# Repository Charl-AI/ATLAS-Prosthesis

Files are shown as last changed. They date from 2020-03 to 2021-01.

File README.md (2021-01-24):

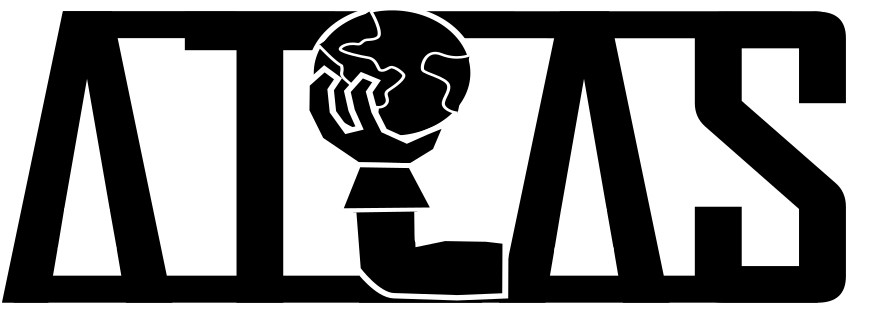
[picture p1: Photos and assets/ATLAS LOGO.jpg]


Modern solutions for control of prosthetic hands involve sensing intentional muscle contractions using myoelectric (EMG) muscle sensing. Unfortunately this is expensive - with modern electro-mechanical prostheses starting at around £ 10 000 - and sensitive to issues such as perspiration and sensor placement.

ATLAS is a novel prosthetic hand using mechanomyographic (MMG) muscle sensing to control the device. It is fully 3D printable and can be manufactured for under £ 300. The only requirements for reproducing this project are access to a 3D printer (such as the Creality Ender 3 that we used, £ 150) and a soldering station (roughly £ 10).

This project was completed as a university project by four members (and achieved an A grade) and there is plenty of scope for people to adapt and improve our work. The project is documented on this page, however, names and identifying information about the group members have been redacted in some places for privacy.



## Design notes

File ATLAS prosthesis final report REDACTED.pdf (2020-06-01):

## Design, Make & Test Project:

# Final Report

### Mechanomyographic-controlled prosthetic hand

78 Pages | 03/06/20

Group 19

Supervisor:

Charles Jones

Page ii

EXECUTIVE SUMMARY

Transradial (below elbow) amputation can be a debilitating condition, making many tasks associated

with daily life considerably more difficult for amputees. Prosthetic hands aim to mitigate this issue

by providing amputees with a device which can assist in performing complex functions such as

grasping objects. However, the limiting factor in upper body prosthetic design has long been the

shortfall in control systems, preventing amputees from controlling complex machines such as fully

articulated prosthetic hands. Modern solutions to this problem primarily involve using

electromyographic (EMG) sensing to pick up on intentional muscle signals and control the device,

although this method has considerable disadvantages such as perspiration and sensor placement

affecting the results. Moreover, EMG solutions on the market today start at a prohibitively expensive

price point of around £ 10,000. This design, make and test project introduces ATLAS, a novel solution

using mechanomyographic (MMG) muscle sensing to control the device (shown in Figure 1). The

prosthetic hand can form three user-controlled grip poses (point, grasp, and open), controlled

through a specially designed MMG-sensing armband which was demonstrated to produce up to

90 % muscle sensing accuracy when tested virtually with a dataset of 17 labelled muscle movements

over 6 different muscles. The mechanical design of ATLAS draws from fields such as soft robotics and

biomimetic design, using a composite structure that enables grasping of a variety of hard, soft and

irregularly shaped items with robust functionality: in testing, ATLAS was able to pick up objects of

over 3.5 kg with ease. ATLAS is fully 3-D printable and can be manufactured for under £240, lending

itself to an open-source, distributed manufacture model of production, specifically intended to be of

most benefit to amputees in developing countries and children. Unfortunately, the unprecedented

coronavirus outbreak cut short the practical time available for this project, however, all possible

steps were taken to mitigate this effect and an alternative work package was completed to ensure

the project remained of high quality despite these setbacks.

Figure 1: ATLAS (without electronics or sensors)

Page iii

CONTENTS

Executive Summary | ii
Contents | iii
Acknowledgements | iv
1 | Introduction | 1
1.1 | Brief | 1
1.2 | Team Roles | 1
1.3 | Report Structure | 2
2 | Literature Review and project background | 3
2.1 | Transradial amputations and needs of amputees | 3
2.2 | Principles and paradigms of upper body prostheses | 3
2.3 | Mechanomyographic techniques for muscle sensing | 5
3 | Design | 7
3.1 | Product Design Specification | 7
3.2 | Expert Research Meetings | 9
3.3 | Conceptual Design | 10
3.4 | Mechanical Design | 14
3.5 | Control Design | 23
3.6 | Electronic Design | 31
3.7 | Final Design | 36
4 | Manufacture and Assembly | 37
4.1 | Methods and Justification | 37
4.2 | Mechanical characteristics of FDM printed parts | 38
4.3 | Design for 3-D Printing | 38
4.4 | Printing with PETG, PLA and TPU | 42
4.5 | Assembly of electronics | 43
4.6 | Overall assembly | 43
5 | Product Cost and Budget | 45
5.1 | Finance and budgets | 45
5.2 | Final Product Cost | 45
6 | Testing and Design Verification | 47
6.1 | Destructive Testing | 47
6.2 | Grip Strength Test | 50
6.3 | User Testing | 51
7 | Alternative Work Package | 52
7.1 | Effect of early university shutdown on project | 52
7.2 | Details of uncompleted tasks | 52

Page iv

7.3 | Details of alternative work package | 53
7.4 | Alternative Work | 53
8 | Discussion | 59
8.1 | PDS Evaluation | 59
8.2 | General Discussion | 61
8.3 | Future Work | 64
9 | Conclusions | 65
10 | Personal Reflective Reviews | 66
10.1 | | Error! Bookmark not defined.
10.2 | | 67
10.3 | | Error! Bookmark not defined.
10.4 | | Error! Bookmark not defined.
11 | References | 70

ACKNOWLEDGEMENTS

The group would like to extend our warm thanks to the following people and companies:

1 | INTRODUCTION
1.1 | BRIEF

Today’s market for upper body prosthetics is broadly divided into high-cost, high

sophistication, electro-mechanical designs, and low-cost body-powered devices with less

functionality (elaborated upon in the literature review, section 2). This project aims to bring the

advantages of electromechanical prostheses to consumers at a significantly lower price point by

exploiting two emerging techniques: mechanomyographic (MMG) muscle sensing and open source

distributed manufacturing. At the beginning of the project, the following five targets were set out:

- Design and manufacture a prosthetic hand capable of forming multiple useful grip patterns.
- Design a comfortable strap to house muscle sensors and a basic socket to suspend the

device from a demonstration stand.

- Sense and analyse MMG muscle signals, producing an algorithm to accurately classify muscle

contractions.

- Implement a control system so the user can accurately move between the grip patterns by

utilising intentional muscle movements.

- The final product must be manufacturable by volunteer engineers or hobbyists at a low

price.

These ambitious targets are designed to enable the creation of a new class of prosthetic device –

one which can bring the functionality associated with high-cost prostheses but be open-sourced

and manufactured at a low cost by amputees themselves or volunteers.

1.2 TEAM ROLES

Although all members of the team contributed to many aspects of the project, and supported each

other wherever necessary, a summary of primary roles are listed below, together with the headline

requirements and responsibilities of the role. Team members had a management role which

supported the organisation of the team and project, as well as a technical role. These were allocated

based on previous project experience, areas team members wanted to focus on, and ME1/2/3

module experience, and are listed below in Table 1.

Table 1: Team roles and responsibilities

Name | Management Role | Technical Role
| Project Manager | Electrical Lead
| Ultimately responsible for ensuring all elements of | Lead for the design, testing, build and
| the project progress on track and to a suitable | assembly of physical electronics.
standard, in line with internal and external
deadlines, and allocating resources to ensure that
deadlines are met.
Meeting Coordinator
In charge of organising group meetings and room bookings.

Manufacturing Lead
Responsible | for | manufacture | and
printing, and also for providing input on design for additive manufacturing to the mechanical design process.
| Procurement + Finance Lead | Mechanical Design Lead
| Responsible for managing, facilitating and | Lead on design process, bringing together
| approving purchase requests (together with the | work from other team members
| PM), and ensuring expenditure remains within | regarding product design from inception
| budget and restrained. | right through to final prototype stage.
Charles
Jones

Document Lead
In control of overall document management, including Quality Plan, Progress Report and Final Report, and creating timelines to ensure these are produced on time.

Coding Lead
Responsible for all software elements of the design, from signal acquisition and processing to digital user experience design.

1.3 REPORT STRUCTURE

This report aims to present the final product, ATLAS, and the care and attention invested into all

three areas of design, make and test. It begins with a literature review, outlining the market need for

a product of this type, the background of the market, and consideration of different prosthetic

control methods. Section 3 addresses the design progression, covering the full process from

conception to detailed design of the mechanical, electrical and control systems of the device. It is

important to note that ATLAS was explicitly designed using a continuous, iterative cycle of

prototyping and testing, so this section includes many of the tests which were performed to inform

design decisions. Section 4 details the manufacture of the product, explaining the methods and

materials chosen, alongside considerations made when designing with these in mind. Section 6 then

documents the testing performed to verify design decisions, refine areas of the product and to

evaluate if the product performs as specified. This project was unusual in that it was interrupted by a

complete shutdown of practical university work in response to the unfolding pandemic COVID-19, so

a section was included to discuss the effects of the shutdown on the project and provide alternative

work to replace the work that was cut short. The discussion and conclusions follow, and the report

finishes with personal testimonials from each of the four group members

2 LITERATURE REVIEW AND PROJECT BACKGROUND

A literature review was conducted to understand modern prosthetic devices and the market for

them today – first, the prevalence of transradial (below elbow) amputations and the needs of

amputees were established and the principles and challenges of modern prosthetic design were

examined. Finally, the review covers the emergence of mechanomyography (MMG), a novel muscle

sensing technology which is used to control the ATLAS prosthetic hand made by this group.

2.1 TRANSRADIAL AMPUTATIONS AND NEEDS OF AMPUTEES

The dexterity of the human hand to perform complex mechanical tasks possesses no parallel in the

human body; it is often modelled as a machine with 27 independent degrees of freedom (1) and it

has huge versatility – giving it uses in all areas of modern life, including sports, personal care,

cooking, communication and more. The loss of a hand from a transradial amputation is an extremely

debilitating condition which typically occurs after a traumatic injury (2), and maximising quality of

life after such an injury is best achieved through a program of rehabilitation utilising prosthetic

devices to allow the patient to re-learn daily tasks (3). The needs of prosthetic device users are well

known, with studies over the previous 20 years (4,5) corroborating the same few key desires: the

ability to perform tasks such as dressing and eating with knife and fork; anthropomorphic aesthetics;

reliable, high strength grasping with their prosthesis; and comfort using the device.

2.2 PRINCIPLES AND PARADIGMS OF UPPER BODY PROSTHESES

Mechanical design of fully articulated, anthropomorphic hands is, in principle, straightforward.

These devices exist in robotics development (reviewed in (6)). However, prosthetic devices have yet

to match the ability for independent finger articulation of these robots. This is in large part due to

control systems and the interface between the user and the machine lacking the necessary

complexity to allow control in all 27 degrees of freedom. The two main control methods used in

prosthetic devices on the market today are body-powered control and electromyographic (EMG)

control.

Body-powered prostheses rely on the user providing the power and control of movement by

physically actuating the device’s mechanism (often using a harness and tension cable system which

the user pushes against). The most common type of body-powered prosthetic device is the split

hook, depicted in Figure 2(A) – these provide a durable solution which give the amputee the ability

to perform simple grasping movements. Unfortunately, however, their functionality does not extend

much further than that, which is a key reason why many amputees abandon their prostheses entirely. As many as 56 % of upper limb amputees wear their prosthetic limb ‘once in a while’ or

‘never’ and 64 % of amputees rate the functionality of them as ‘fair’ or ‘not acceptable’ (7) – this

high rejection rate, combined with the poor aesthetics of split hooks, has meant they have begun to

fall out of favour in recent years.

Electromyographic-controlled prostheses (also known as myoelectric or EMG), depicted in Figure

2(B), are a more modern solution and typically show lower rates of user rejection than body-

powered prostheses (8). These devices allow the user to control an electronically powered

prosthetic hand by using voluntary muscle contractions that are picked up by electrodes, which can

be placed on the surface of the skin, as reviewed in (9), or implanted into the user’s forearm muscles

(as in (10)). These devices typically have several pre-programmed grip patterns which the user can

move between, giving them superior functionality to body-powered prostheses. Arguably the most

significant issue with the myoelectric prostheses available on the market today is their prohibitively

high price point, typically of the order of £10,000 and upwards – naturally, this has spurred

significant research interest in developing low-cost alternatives to these products (11-13), however,

none of these lower-cost products have yet proven to be viable as a long-term solution for

amputees.

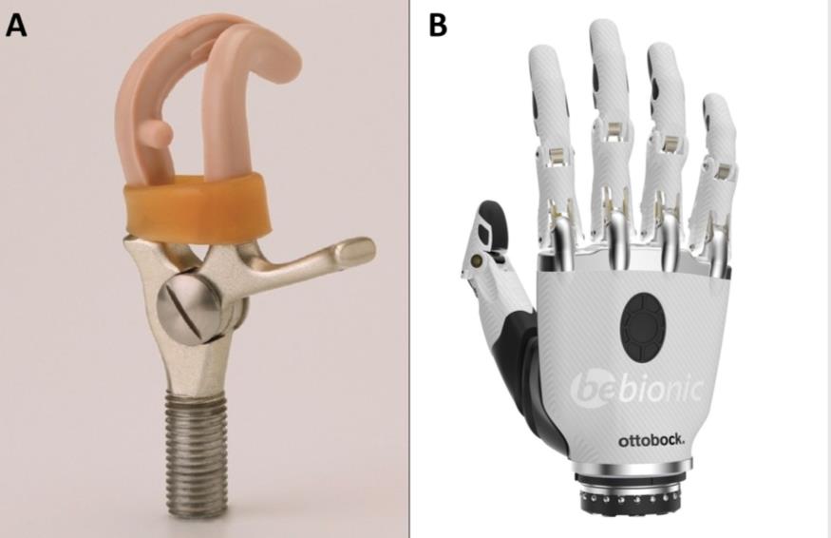
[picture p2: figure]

Figure 2: Body-powered split hook prosthesis (A), adapted from figure 2 of (14). Ottobock BeBionic myoelectric prosthesis

(B), figure from ottobockus.com (15).

Thus, amputees are today faced with a difficult choice when selecting between devices – either

choose a mechanical device with high reliability but limited functionality or have to part with

potentially tens of thousands of pounds for a myoelectric device. This problem is exacerbated when

considering that many countries do not have health services that will purchase these devices for amputees; moreover, children are often denied expensive devices because the investment is too

great for a product which they will grow out of in a couple of years. A brief comparison of several

notable myoelectric products, and a well-known open-source mechanical design, are presented

below in Table 2, illustrating the wide range of price-points and functionality.

Table 2: Comparison of variety of products on the market

Product,

[Manufacturer]

Cost | Product information

Michelangelo

hand [Ottobock]

£ 46,000 | Aesthetically pleasing design with a silicone glove for added
| realism. Hand can perform 7 pre-set grips and models the
| action of bones and joints.

Bebionic

[Ottobock]

£9,000 | The hand is capable of 14 grip patterns, with actuation on each
| individual digit, and an adjustable hand position.

Hero Arm [Open

Bionics]

£5,000 | This is the cheapest myoelectric device on the market, in part
| due to its 3-D printed design. However, it has not yet been
| approved by the NHS in the UK.

Phoenix Hand [E-

NABLE]

£50 | A 3-D printed, open source, body-powered design. Low
| functionality and low durability.

One further challenge of prosthesis design is the suspension of the device from the amputee.

Modern devices typically use one of three techniques for prosthesis suspension: self-suspended,

suction methods, and harness methods. The advantages and disadvantages of each method are

discussed in (16) and (17) provides a review on the topic of prosthetic interface and its effect on

comfort. This area of prosthetic design, however, is not the focus of this DMT project, so will not be

discussed any further in this review.

2.3 MECHANOMYOGRAPHIC TECHNIQUES FOR MUSCLE SENSING

One alternative to the paradigms of body-powered and EMG prostheses that has gained traction in

recent years is mechanomyographic-controlled (MMG) prosthetics. MMG muscle sensing relies on

sensing low-frequency, mechanical vibrations generated by muscles during a voluntary contraction

and has been shown to produce comparable results to traditional EMG sensing (18-20). Although

EMG is typically considered the gold standard for muscle sensing, MMG methods have several practical advantages that suit use in a prosthetic hand, including low sensitivity to changes in skin

impedance and low sensitivity to non-optimal sensor placement – both of which are well-known

problems with EMG sensing (21,22). The nature of MMG signals as vibrations also means that the

hardware requirements for MMG sensing are simple and low-cost, requiring only microphones with

no amplification necessary.

Despite these advantages, there have been relatively few attempts to develop a prosthetic hand

controlled by these signals, with notable research coming from Imperial College London’s

Biomechatronics laboratory (23,24). A spin-off company from Imperial, SERG technologies, has

recently begun development into this very field, so it is the authors’ hope that commercial MMG-

controlled prosthetics will become available in the coming years.

3 DESIGN

The first major step in the engineering process was the actual design of the product. Initially,

quantifiable targets for the project were set out in the PDS. From there, concepts were developed,

and a morphological analysis conducted upon the different aspects of the concepts. The design was

then split into mechanical, electrical and control streams; each being designed largely in parallel with

all sections coming together in the final design.

3.1 PRODUCT DESIGN SPECIFICATION

The first stage of the design process involved constructing a product design specification (PDS),

shown in Table 3. This was produced from the targets set out in the brief (section 1.1), using insight

gained from the literature review (section 2); the PDS sets out quantitative objectives that the

product can be designed for and tested against to ensure high quality through the design, make and

test process. Naturally, due to the number of unknowns at the beginning of the project, the PDS was

refined several times due to increased knowledge about the technical aspects of the project, a topic

elaborated upon in the project progress report and quality plan documents (25,26). Aspects which

were subject to change are marked with an asterisk and the history and reasons for the change are

more fully explained in the progress report.

Some aspects of the PDS are crucial for successful delivery of the project targets, whereas other

aspects are less important either because they do not affect the project as much or because the

objective was chosen as an arbitrary target. To create a clear demarcation between these three

levels of importance, the aspect section of the PDS was color coded, with green aspects being crucial

to the project performance, yellow aspects being important, but arbitrarily chosen goals and blue

aspects being non-critical to the delivery of the final product.

Table 3: Product Design Specification

Aspect | Objective | Justification | Verification
Number of grip poses* | ≥ 3 | Three poses should provide sufficient functionality for key uses in daily life. | Design review.
Maximum grip force | ≥ 30 N | 30 N is suitable for basic daily tasks such as carrying shopping and shaking hands. | Prototype testing using force meter.
Sensing method | MMG | MMG sensing will be used for signal acquisition. | Design review.
Gesture recognition accuracy | 90 % | For the device to be useable daily, it must correctly actuate 90 % of the time to avoid user frustration. | Prototype testing.
Battery life | 12 hours | 12 hours of continuous use would last through a full workday and use at home. | Prototype testing.
Product lifespan | 2 years | Operate for a minimum of 2 years before failure under standard use. | Fatigue testing of prototype.
Waterproofing | IP33 rating | This should allow for protection from splashes and small solid objects. | Test prototype against standards.
Form factor | Adult sized right hand | The device should fit adult transradial amputees. A basic socket will also be designed for demonstration purposes, although this is not the focus of this project. | Design review.
Mass | < 500g | An average human hand has a mass of approximately 500g. This should therefore be a reasonable upper limit for the product mass, to avoid user discomfort. | Weigh prototype with digital balance.
Maximum electronics temperature | < 40 °C | Skin-contact and external surface temperatures must remain under 40 °C to avoid potential discomfort and burns (based on ASTM C1055 standards (27)). | Run for 10 mins then scan with infrared thermometer.
Transmission enclosure | Enclosed | Transmission parts should be enclosed for the user’s safety. | Design review.
Electronics enclosure | Enclosed | Electronics should be enclosed to minimise the chances of burns and shocks. | Design review.
Loading | ≥ 50 N | The mechanism must not break when overloaded. | Perform loading test on prototype.
Quantity | ≥ 2 | An initial working prototype will be made followed by a final product. | Count prototypes.
Cost* | < £400 | If the final device has a materials cost of less than £400, it will be accessible to users with a wide range of economic circumstances. | Summing cost from bill of materials.
Materials* | Cheap and widely available materials | Material selection will occur at a later project stage and will be intertwined with the manufacturing processes chosen. | Design review.
Processes | 3-D printing and related methods | The product must be manufacturable by volunteer hobbyists and engineers using methods reasonably accessible to them. | Design review.
Assembly | < 3 hours | Must be assembled and fitted to an amputee in less than three hours by an engineer. | Timed test with stopwatch.
Training | <30 mins | New users should be able to learn the basics of controlling the system quickly to avoid frustration. | Timed test with stopwatch.

Performance

Life

Size

Safety

Production

3.2 EXPERT RESEARCH MEETINGS

Early in the design process, we decided to organise meetings with experts in fields relevant to this

project. Fortunately, both Alex Lewis and Liang He kindly offered us their time and meetings with

them yielded some extremely valuable insights into different areas of the design. The first meeting

was with Alex Lewis, a quadruple amputee who sits on the board of directors of SERG technologies

(a spin off company from Imperial focussing on the uses of mechanomyography). Liang He, who we

met in the second meeting, is a soft robotics PhD student from Imperial’s Dyson school of Design

Engineering.

3.2.1 MEETING WITH ALEX LEWIS

The key insights from the meeting with Alex were:

| • He had found that the robustness and versatility of non-mechanical prosthetics is a major
| issue; for day-to-day use, he uses a mechanical split-hook.
| • Having a prosthetic capable of multiple, simple day-to-day tasks would be beneficial.
| Examples he gave included: picking up a glass, moving a variety of objects around, or holding
| cutlery.
| • In his opinion, the performance of a prosthetic is far more important than how it looked; he
| believed that this opinion was held by most amputees, including children as well as adults.

3.2.2 MEETING WITH LIANG HE

The aim of the meeting with Liang He was to gain more of an insight into how soft robotics like those

used in medical procedures could influence a prosthetic design. The key insight was that for an

electromechanically controlled prosthetic, the stiffness of the composite finger design is a major

design variable and would need careful consideration. He also discussed haptic feedback, and the

various methods that could be delivered (through mechanical vibration, sound, or electrical

stimulation), but noted this could be a complex addition to the project. It was also noted that

electrical or mechanical stimulation near the MMG sensors could cause significant interference.

3.3 CONCEPTUAL DESIGN

During conceptual design, it is important to generate a wide range of ideas, taking many forms and

using different mechanisms and technologies to solve the same problems. This section details the

process followed when considering different concepts and ideas, using a morphological chart to aid

decision making and produce a final concept.

3.3.1 IDEATION

Figure 3 displays some early stage annotated ideas, which were then developed into the first

concepts. Some key considerations are how many digits the hand has, how the digits are actuated

and the grasping mechanism.

Figure 3: Selection of initial ideas

3.3.2 INITIAL CONCEPTS

This section introduces 3 of the most interesting concepts produced in this process. These were

influential in constructing the morphological chart, which includes aspects from each of these

concepts and more.

The first concept, shown in Figure 4, is a design with 5 digits. The 4 fingers are connected to a linear

motor with tendons and the force is distributed equally across them using a ‘whippletree’

mechanism. The thumb is actuated by a separate linear motor on the underside of the hand and the

fingers have a design of 3 phalanges per digit (meaning 3 independently articulated sections). The

benefit of this design is that by having only two motors, the cost for electronics would be low;

however, the drawback would be that there is less scope for different poses, as the four fingers

cannot be actuated independently.

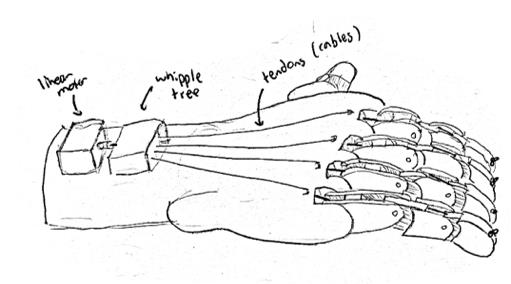
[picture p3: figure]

Figure 4: Concept 1

Figure 5 shows a second 5-digit concept. Each finger has two phalanges, which are actuated by a DC

motor using worm gears and linkages. The design also contains a rotating wrist, and a pivoting

thumb. The main benefit of this design would be the scope for many different grip poses, and the

dexterity that would provide. However, the drawback would be that the design is quite complex

mechanically and electronically, and thus likely quite expensive and difficult to manufacture.

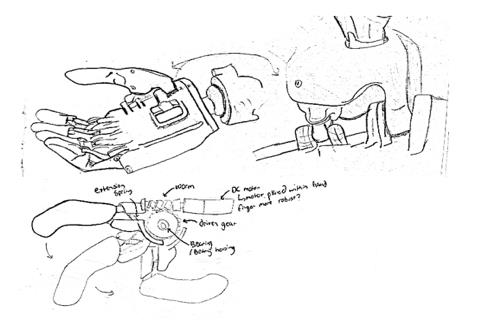
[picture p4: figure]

Figure 5: Concept 2

The third concept (Figure 6) is focussed on the digits themselves. In this concept, the fingers are

based off human biology, where hard bones lend rigidity and a soft outer skin gives grip and

durability. The advantages of this approach are self-evident as the concept could, in theory, come the closest to matching the capabilities of human fingers. There is, however, increased design

complexity and care would be necessary to tune the ratios of hard and soft material.

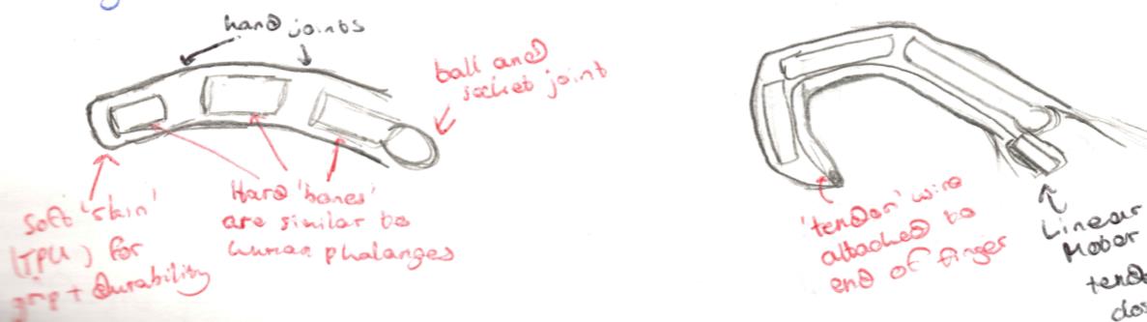
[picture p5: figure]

Figure 6: Concept 3

3.3.3 MORPHOLOGICAL ANALYSIS

After the initial conceptual design, a morphological analysis was conducted to identify the many

possible variations of the key features of the product. This involved splitting the prosthesis into sub-

features and design elements, and listing various concepts proposed to meet them. Using a ranking

and weighting technique, the most suitable concept was selected for each aspect. Some features,

such as haptic feedback, were decided as potentially unrealistic with the time and resources

available and it was agreed to put them on hold, only considering their addition if significant time

opened up later in the project. Table 4 displays the morphological chart produced, with the selected

concepts highlighted in green and a qualitative explanation of the key design decisions is below.

Table 4: Morphological chart for overall design

Sub-feature | Concept 1 | Concept 2 | Concept 3 | Concept 4
Grip Type (No. of digits) | 5 | 3 | Split hook | Mitten
Digit characteristic | Hard / Stiff | Soft | Compound
Actuation | Tendon | Linkage / Pushrod | Gears
Motor Type | Linear | Rotary | Stepper | Electromagnets
No. of phalanges | 1 | 2 | 3 | 4
Socket design | Forming | Foam and Straps | Airbag

Thumb – Degrees of

Freedom

1 DOF | 2 DOF | Fixed (0 DOF)
Wrist Rotation | Yes | No
Feedback | None | Haptic | Electric | Auditory
- Grip type: it was clear from the meeting with Alex Lewis that function is more important

than form, therefore a 3-finger design was chosen for the final concept to reduce design

complexity whilst maintaining function.

- Digit characteristic: Having a composite biomimetic design of hard ‘bones’ and soft ‘skin’

was deemed an exciting and effective avenue for development.

- Actuation: A simple but robust design of linear motors driving tendon cables was decided.
- Number of phalanges: In keeping with the biomimetic design, 3 phalanges were used. This

style allows the fingers to bend into a good shape for grasping objects.

- Socket design: Socket design was not considered to be a key focus of this project, so a

simple concept was chosen for use with a display stand.

3.3.4 FINAL CONCEPT

The final concept invoked from the morphological analysis is depicted in Figure 7. This concept

involves a hand with three fingers, each with hard and soft components to mimic the human hand.

The fingers are actuated using tendon wires driven by linear motors and a simple socket is included

for demonstration and testing.

Figure 7 - Final Concept

3.4 MECHANICAL DESIGN

This section details the mechanical design of the product and the reasoning, iteration and

calculations involved in this process. A philosophy of rapid prototyping using 3-D printing was used,

allowing small design, make and test cycles to drive iteration and improvement. The ambitious

nature of our PDS made calculation and logical reasoning crucial to the design process.

3.4.1 MATERIAL SELECTION

When designing the product, material selection was an important parameter, considered from the

very start of the process. One of the aims of this project set out in the brief is for the final product to

be manufacturable by a volunteer hobbyist or engineer – so the main manufacturing method chosen

was 3-D printing (explained in full in section 4.1).

There are three main groups of filaments for printers: standard solid filaments; flexible filaments;

and exotic particulate filaments. A standard solid filament is a filament which is made from one main

plastic and occasionally a bonding agent. They can usually extend by up to around 25 % before fast

brittle facture occurs. A flexible filament is the same as the solid filament in the sense that it is one

main plastic, however it has a maximum elongation above 400% before failure. So-called ‘exotic

particulate’ filaments are a mix of a plastic with a filler, for example wood fibres or graphite, which

add properties such as electrical conductivity or increased strength. Although creating a material

with electrical conductivity would mean the electrical connections could be printed directly into the

parts, this would require a dual extrusion printer (to produce the conductive / not-conductive

sections in parallel) which goes outside of our PDS, as dual-extrusion is not a common entry-level

3-D Printer.

There were three material selections that needed to be made. They are listed below, along with the

requirements:

| • Socket – Requirements: mouldable at relatively low temperatures (achievable without
| specialist equipment), but not so low that the form could change under normal use,
| relatively tough, relatively light.
| • Outer finger ‘skin’ – Requirements: flexible with high durability and toughness
| • Rest of product – Requirements: hard, low-density, tough (retaining these characteristics
| within the expected operating temperature range).

After some research, we decided to use three different materials: Polylactic Acid (PLA) for the

socket; Thermoplastic Polyurethane (TPU) for the fingers; and Polyethylene Terephthalate Glycol

(PETG) for the rest of the product. A summary of the properties of each of these plastics can be seen

below in Table 5. These properties are for a homogenous piece and will not quite reflect the

properties of a fused-deposition product. Thus, as part of the design validation process, the actual

strength of our parts was tested, as can be seen in section 4.3.1 and section 6.1.

Table 5: Summary of PLA, PETG & TPU Material Properties. Values taken from (28).

| PLA | PETG | TPU
General Classification | Standard solid filament | Flexible Filament

Density (g/cm³
) | 1.29 | 1.28 | 1.21
UTS (MPa) | 46.8 | 48 | 38.1
Elongation at Break (%) | 62.9 | 59 | 549
Young’s Modulus (GPa) | 2.8 | 2.83 | 0.147
Print Temperature (oC) | 180 | 250 | 200
Softening Temperature (oC) | 71.7 | 92 | 105
Glass Transition Temperature (oC) | 52.6 | 83 | -21.8
Average Cost per Kilogram (£) | 20 | 25 | 25

3.4.2 FINGER DESIGN

The use of an iterative design process on the fingers was extremely beneficial. The finger concept

was chosen to be a composite design of hard interior ‘bones’ and soft outer ‘skin’, actuated by a

linear motor which pulls a tendon wire (made from fishing wire). Flexible TPU filament was chosen

for the soft skin, with PETG for the hard bones. The stiffness of the fingers is a key design parameter,

as they must be able to deform when the tendon wire pulls them, however, be stiff enough to grasp

heavy objects. The complex deformations involved with this design made accurate analytical

calculation impossible – so prototypes were designed, 3-D printed and tested as part of the iterative

design process – a diagram of the changes to the finger design as this process progressed can be

seen below in Figure 8.

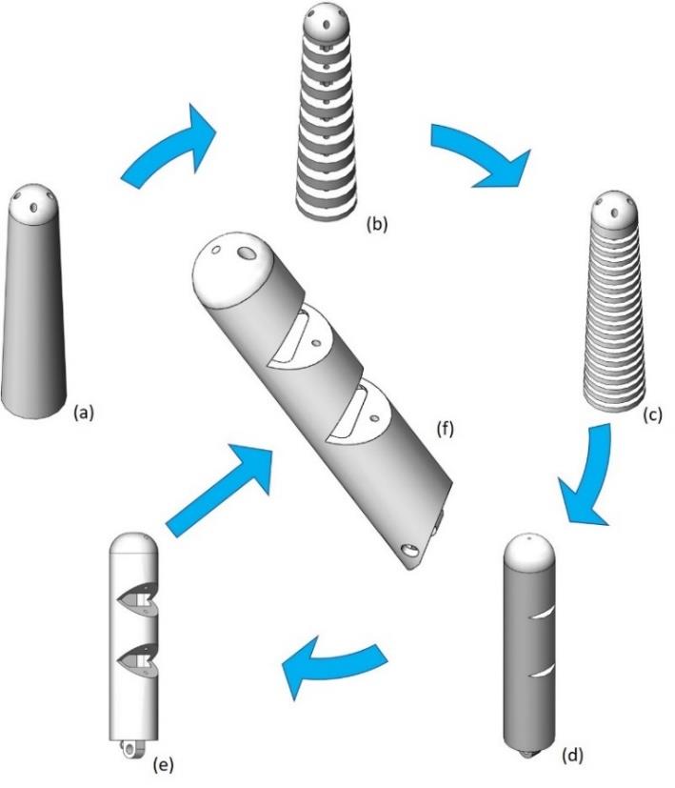
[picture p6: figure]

Figure 8: Iterative design of the flexi-finger

a) The first iteration was a completely solid piece of TPU, with four holes for the threading of

fishing wire to control its motion. The design, when printed, was too stiff to bend easily and

therefore some material needed to be removed to decrease the second moment of area –

explained by | Equation 1 which models the initial

deformation as buckling of a strut under an off-centre load, Pc. By reducing the second

moment of area, we can thus reduce the necessary force and hence reduce the effective

stiffness of the finger.

Pc =

π

2EI
4L
2 | ⟹ Pc ∝ I | Equation 1
b) The second iteration had two types of sections with different second moments of area. One

with a smaller second moment of area as it has a smaller cross-sectional area, the rest of the

finger has the same cross-sectional area as the first iteration. The finger was easier to bend

than the first iteration, however the force required to bend was still too high. One way of

adjusting the stiffness of the finger was to vary the infill density of the part. By changing this

parameter, an infill of 10% was found to be most suitable.

c) The third iteration had the same types of sections as the second, however the more of the

finger was of the smaller cross-sectional area. This finger suffered the reverse problem of the previous iterations, with too little stiffness. This iteration struggled to grip objects

because it would simply splay out away from them.

d) This iteration had an internal bone structure which was designed to prevent sideways

movement. The wire was routed through the bone structure (based off another prosthetic

hand design we had seen). However, there were two main issues with this design. The

removed material designed to reduce the second moment of area did not reduce it enough

and having the wire inside the bones meant the wire plastically deformed during bending.

e) This iteration corrected all the issues found in iteration (d) by increasing the cut-out size and

moving the wire to attach to the outer flexible part of the finger. This finger worked as

desired.

f) The final iteration had added features for aesthetic and grip improvement purposes. The

slope at the bottom makes the whole finger appear flush to the overall hand and a recess

was added at the top of the finger to enable a knot in the wire to sit flush with the surface of

the finger. The fishing wire is actuated by the linear motor and causes bending due to the

force being applied to the tip being off-centre.

3.4.3 PALM DESIGN

The ‘palm’ section of the device is important because it contains the electronics, the motors, and the

battery. It also provides attachment points for the fingers and influences the mechanics of how the

device grasps objects. This was a complex section to design and consists of three parts: a base which

houses the motors, provides attachment points for the fingers and channels the tendon cables; a

mid-plate which sits over the motors and provides a platform for electronic components; and the

cover which simply encloses the structure.

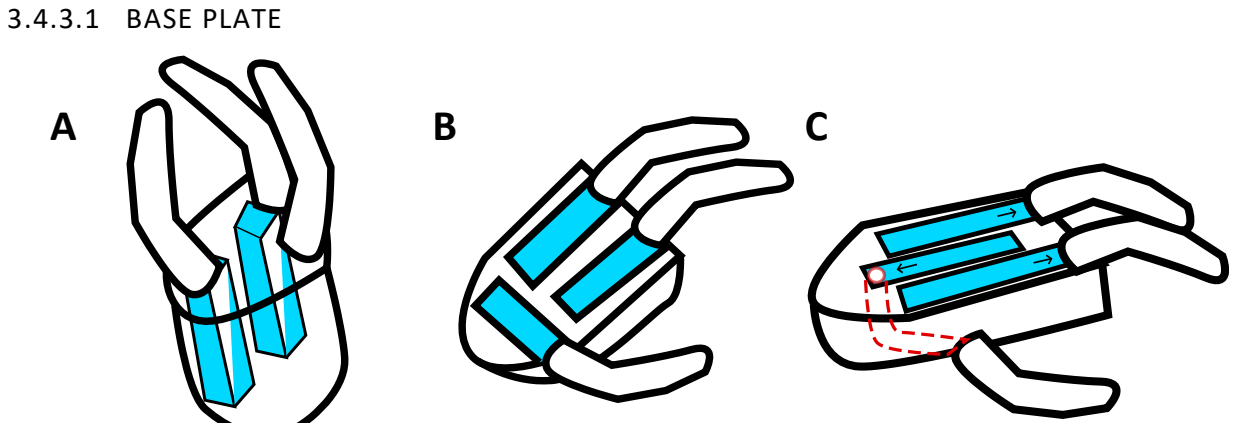
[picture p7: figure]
3.4.3.1 BASE PLATE

Figure 9 - Concepts for motor placement: (a) face mounted (b) perpendicular mounting (c) parallel mounting

One challenge when designing the base plate was arranging the motors in a space efficient way.

Three possible design solutions are shown in Figure 9. (a) Shows face mounted fingers, with the

motors held within the base section. The overhang features and the complexity of assembly were

the main issues with the proposal. (b) Shows a concept where two fingers come out the top, with

the motors in parallel, and the thumb mounted on the side, with the motor perpendicular to the

rest. The issues with this design were that it required a large surface area to mount all the motors,

and the efficacy of the thumb for gripping was poor. (c) Shows a concept with all three motors

parallel with the centre motor in reverse, connected to the thumb on the base of the hand. This was

the chosen design as it has the smallest area for all the mounting, with the simplest assembly while

maintain a high potential for gripping objects.

Once the motor placement was chosen, the most important design feature was the exact location

and spacing of each digit. Through analysing a simplified version of the paths each the finger and

thumb would follow, the optimal positioning for grabbing was determined. The path mapping also

demonstrates how handles such as those on shopping bags can be grasped easily before being held

by the grip.

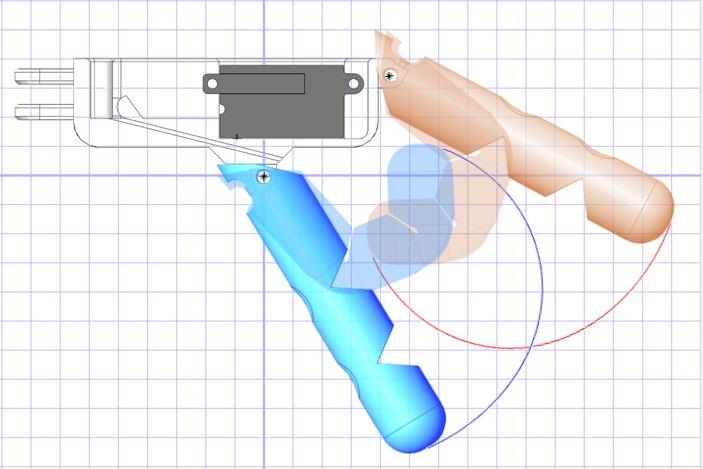
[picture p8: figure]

Figure 10 - Approximate path of fingers (orange) and thumb (blue)

Figure 10 shows the path followed by each digit. The end position of the fully flexed digits show that

they will form a fully closed overlapping ‘clench’, a good grip for picking up objects in everyday life as

specified in our PDS. Moreover, there is space between the palm and the fingers to hold objects or

handles in the fully closed position. This analytical approach was supported by real-world evidence,

attained by producing a working prototype (described in full in 3.4.7). The prototype confirmed the

efficacy of this finger positioning and allowed some fine tuning of the design when moving to the

final version.

3.4.3.2 MID-PLATE AND COVER

The mid-plate and cover were not designed until after the working prototype was tested. This is

because these parts, although important, are largely cosmetic so were not worked on until after the

design of the base plate had been experimentally verified to work. The role of the mid-plate and

cover is to contain the electronics in a space efficient, aesthetically pleasing package; Figure 11

shows the mid-plate and cover on the final design, with annotations describing the changes made as

a result of the working prototype testing:

Figure 11: Final palm design with annotated features

a) The sides of the hand section were curved to improve the aesthetics of the device, without

minimising structural integrity or function.

b) Logo imprinted into the cover.
c) The fingers moved slightly apart to ensure thumb and fingers can close fully and prevent

friction when moving past each other.

d) The front of the hand was gently sloped to grip objects better.
e) The motors were reoriented to allow easier access to their cables and save space.
f) Extra cut-outs were added for wiring to sit in.
g) The rear was extended so the circuit board and relay could be placed within the main

section of the hand, allowing a lowering of the height of the cover.

h) Five side holes were added to place the LED battery level indicators and a switch. One large

hole was added at the back so that the device could be charged without taking off the cover.

To maintain the waterproofing rating, a block of flexible TPU was printed that could be

pushed in as an interference fit to fill the hole when not in use.

i) The mid-plate was added between the cover and the base plate of the hand to guide wires

and constrain lateral movement of the electronics within the hand.

3.4.4 JOINTS AND FIXTURES

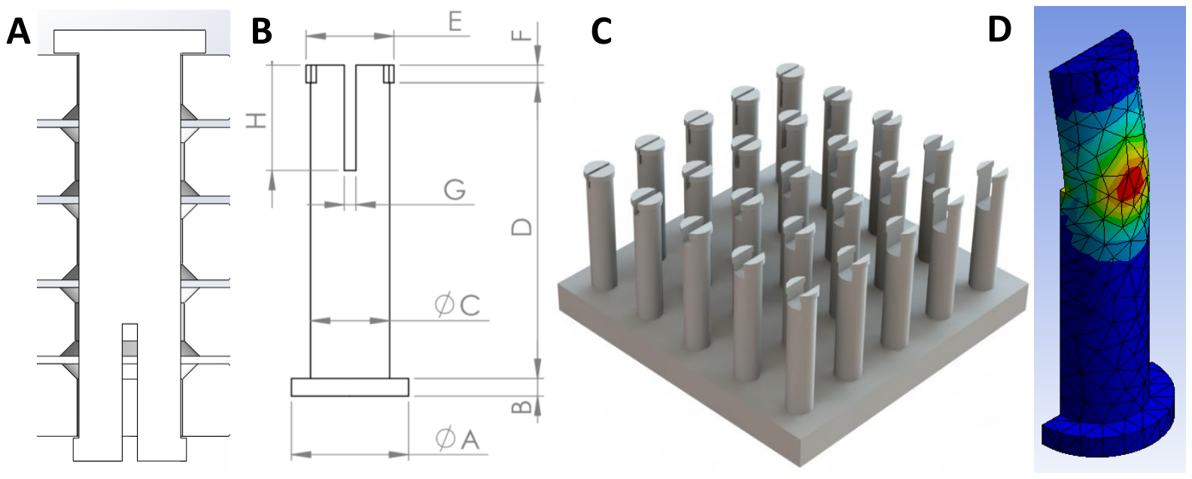
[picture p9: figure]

Figure 12: (A) Pin Locking System. (B) Dimensioning. (C) Pin Testing Rig. (D) FEA of Loading on pin.

The joints connecting the fingers to the palm (‘knuckle’ pins) and connecting the palm to the socket

(‘wrist’ pins) were designed as simple push pins with lips which lock into place, shown in Figure

12(A). These pins, made from PETG, must be able to support the device when under its maximum

load of 50 N (specified in the PDS) and the complex shape of the pins makes analytical calculations

difficult and potentially inaccurate. For this reason, a testing rig, shown in Figure 12(C), was

developed to enable testing of many different pin geometries – resulting in the optimal dimensions

for both the wrist and knuckle pins being found through testing. Once the best pin was found, the

results were validated using a finite element analysis (FEA) study, shown in Figure 12(D). This

demonstrated the location of the weak point in the structure and provided values of the stress at

this point when under loading – giving results of 27.8 MPa for the wrist pins and 32.9 MPa for the

knuckle pins under a 50 N load. This corresponds to safety factors of 17 and 14.6 respectively,

ensuring that the pins were more than strong enough to handle the maximum loading case set out

in the PDS. The final dimensions of the pins are shown in Table 6, referencing the dimensions

labelled in Figure 12(B).

Table 6: Pin Dimensions

Pin type

Dimension (mm)

| A | B | C | D | E | F | G | H
Wrist Pin | 10 | 1.5 | 6.75 | 25 | 7.5 | 1.5 | 1 | 9
Knuckle Pin | 7.5 | 1 | 3.75 | 19.5 | 4.25 | 1 | 0.75 | 7.5

3.4.5 SOCKET DESIGN

As previously mentioned, this project focusses on the hand itself so suspension from the amputee is

not a key part of this project. Socket design is a complex and advanced area of prosthetic design in

its own right, so, a simple approach was taken – designing a basic socket that could be used with a

demonstration stand or with an amputee for testing purposes. The design can be seen below in

Figure 13, consisting of 3-D printed PLA. Although it is printed flat, the part is designed to be thermoformed around the amputee’s stump by submerging it in in hot water above 52.6 oC (the

glass transition temperature for PLA). By wearing an insulating neoprene sleeve, the amputee can

safely form the socket around their stump and get a comfortable, snug fit.

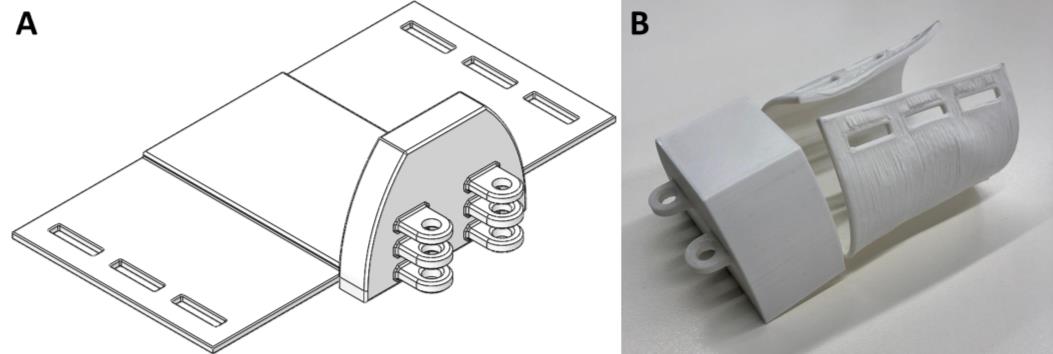
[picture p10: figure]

Figure 13: (A) Socket as printed. (B) Photograph of early stage prototype after thermoforming around a demonstration

stand.

3.4.6 SENSOR STRAP AND CLIPS

Another minor, yet not to be overlooked part of this project was designing a comfortable armband

which the user wears whilst controlling the prosthesis. The armband had to be able to securely hold

the sensors over the correct muscles and allow adjustment for use by different individuals or for use

on different parts of the arm. The design opted for was a 20 mm wide strap, secured in place with a hook and loop (‘Velcro’) mechanism. The sensors sit in small plastic clips which can slide along the

strap; the minimum diameter of the strap was 50 mm and the maximum diameter was 120 mm,

enabling a wide variety of people to use it comfortably. The strap was made from elasticated fabric

to enable it to change diameter slightly while in use – this is important to avoid the strap ‘pinching’

into the user’s muscles as they contract, increasing the diameter of the arm. The assembly of the

strap, clip and sensors is shown in Figure 14 (note: only one sensor is shown in this image, whereas

the strap would typically house two).

Figure 14: Sensor strap with a single sensor in place

3.4.7 MECHANICALLY FUNCTIONING PROTOTYPE

The first functional prototype was made to test the combination of hard and soft materials in the

finger and to look at the overall positioning of the fingers. A render of the prototype and the actual

print can be seen below in Figure 15. During this test, the motors were simply turned on and off to

test the functionality of the mechanical design.

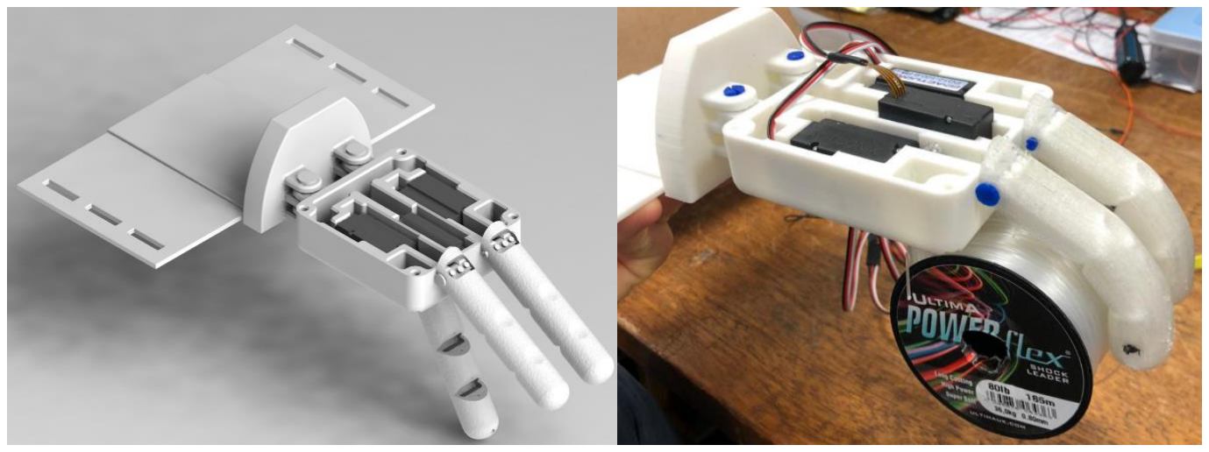
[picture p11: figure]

Figure 15: A render of the working prototype, and it successfully picking up an example object

The hand was successful in holding objects and hence demonstrated the functionality of the

combination of materials. However, it struggled to grip flat surfaces (as opposed to wrapping around objects) and could not fully close. This was due to the positioning of fingers - the two fingers were

too close to each other which meant the thumb could not close at the same time as the fingers.

Therefore, the two fingers were moved slightly further apart for the final design (as mentioned in

section 3.4.3Error! Reference source not found.).

3.5 CONTROL DESIGN

The fundamental principle of operation of this device is that two sensors can be housed in a strap

over an antagonistic muscle pair. Specific movement patterns will cause one or both muscles to

contract, which can be detected by the sensors and converted into a grip pose, as illustrated in

Figure 16.

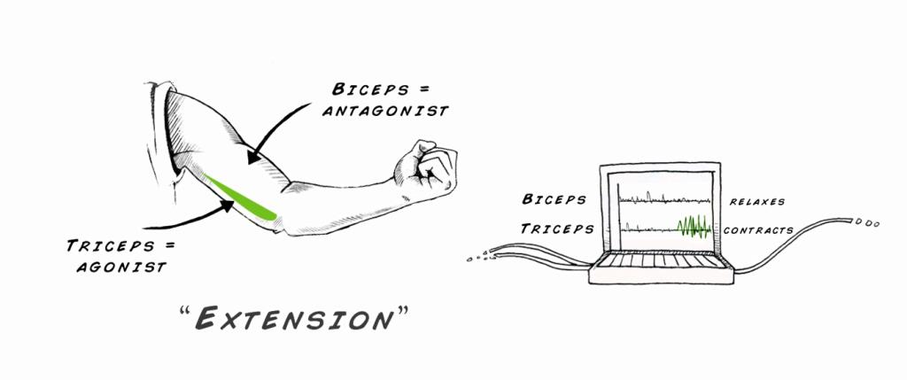
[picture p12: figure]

Figure 16: Basic principles of muscle sensing. Image adapted from (29).

Although this is simple in principle, developing custom software to acquire, process and classify

signals in real time was one of the significant challenges of this project. Successful software should

be able to do this with high accuracy, low latency and not be sensitive to ‘noise’ or non-target

muscle movements. This section details the design of the control systems and software for the final

prosthesis, with the reasoning and technical detail justifying it.

3.5.1 PRELIMINARY TESTS

The first stage in developing the software for the device was to understand the signals being

acquired from the MMG sensors. During this stage of discovery, a single MMG sensor was used in

conjunction with an Arduino UNO board for data acquisition; the signals were then sent through a

serial connection to a Python script where the data could be visualised.

The first test is shown in Figure 17, where the sensor was placed over the brachioradialis muscle of

the test subject and the muscle was activated in four different ways throughout the test. The voltage

output from the sensor was plotted against time for each muscle contraction to make the graphs.

The top-left graph shows the results when no voluntary muscle contraction is performed; from this

data, we can see that there is a messy high frequency noise in the data, as well as a significant 1 Hz

noise (which we believe to be the microphone picking up the subject’s heartbeat). The other three

graphs show more muscle movement types: a three second isometric hold, a fast concentric then

eccentric movement and a slow concentric then eccentric contraction. These graphs all seem to

show a similar pattern – a high frequency, high amplitude set of spikes during the muscle

contraction, immediately followed by a low frequency signal (which seems to represent the muscle

returning to a relaxed state). We want the device to be able to recognise all these contractions as a

user input, so the algorithm should be designed to recognise the low-frequency spike.

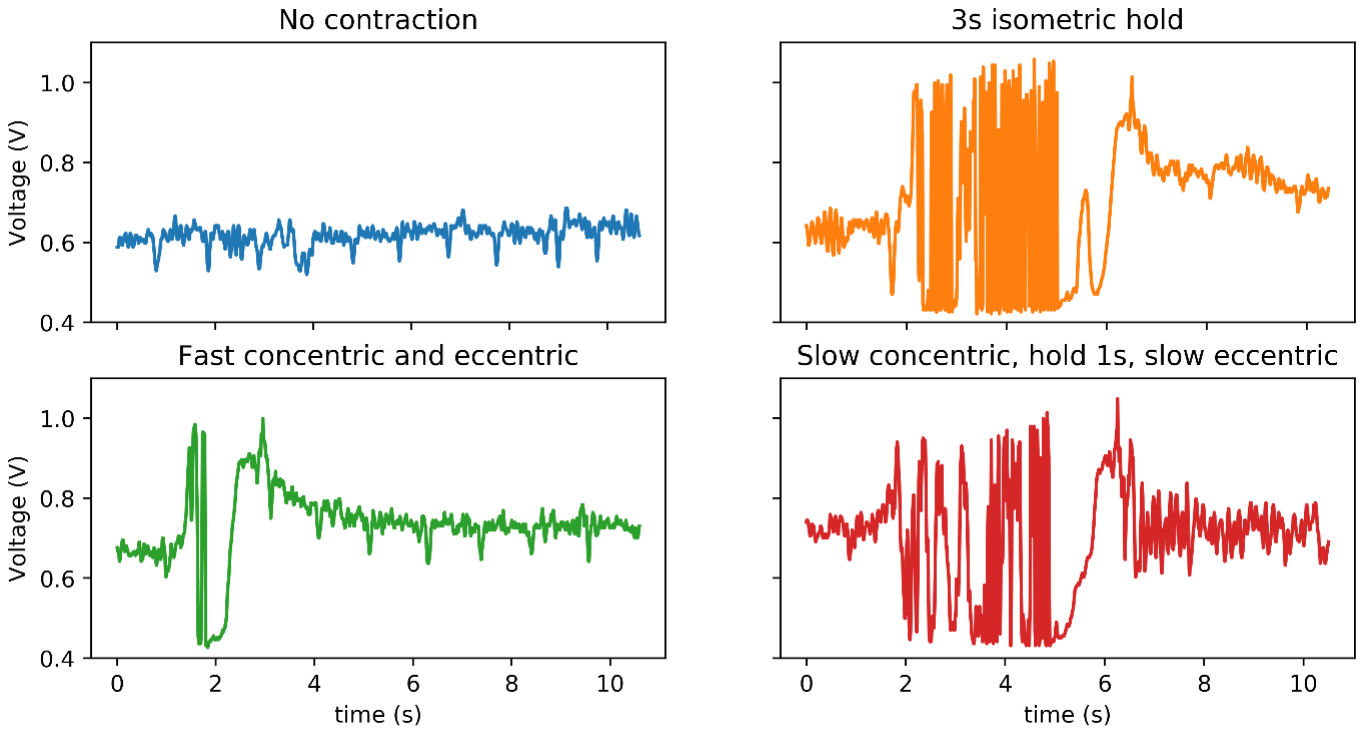
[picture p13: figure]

Figure 17: Raw data acquired from MMG sensors

The next tests were concerned with the optimal placement of the sensors, as well as their sensitivity

to non-target movements. Since both the sensors are housed in a single armband over a muscle pair,

there were three candidate locations for the positioning:

- Forearm (over the flexor digitorum and extensor digitorum pair)
- Below elbow (over the brachioradialis and extensor carpi ulnaris pair)
- Above elbow (over the biceps brachii and triceps brachii pair)

Figure 18 shows the results of these tests for the forearm strap placement. The two graphs on the

left show the response from their respective muscles during the target movement (wrist extension

and flexion). The two graphs on the right-hand side show the response of these muscles for a non-

target movement (in this case, wrist pronation and supination were chosen).

Figure 18: Signals recorded from forearm sensor locations during target and non-target movements

From this data, it is clear that these sensors are very susceptible to noise in the data – meaning that

non-target muscle movements are almost indistinguishable from the target movement in many

cases. This problem was found to be pervasive over all three of the sensor locations, so no location

was deemed to be clearly superior and sensor placement can be decided by the preferences of the

end user.

This problem of noise in the data means that, in order to avoid unintentional device actuation (‘false

positives’), the signal classification algorithm was designed to only recognise muscle contractions

which occurred for longer than a certain period of time. It is unlikely that a non-target muscle

movement would be sustained for a long period, so this enables the device to classify signals into

intentional and non-intentional.

3.5.2 SIGNAL PROCESSING ALGORITHM DESIGN

Once the preliminary tests had been performed, the algorithm for processing and classifying the

signals was designed. The first task was to filter the data – this is important because (as discovered in

the preliminary tests 3.5.1) the important part of the signal is a low frequency spike which occurs

during muscle activation. The final filter design was chosen by consulting the existing literature and

selecting the same setup used in (23) – a fourth order Butterworth band-pass filter (5-100 Hz), with a

sampling frequency of 1 kHz.

Once the signal is filtered, it must then be rectified and smoothed. The approach used in this project

was to take the root mean square over a moving window of data – this is a common strategy used in

EMG signal processing to output a result proportional to the power of the signal in the desired

frequency range (30). The size of the moving window (N) was selected to be 500 samples

(corresponding to 0.5 seconds of data at 1 kHz). This was chosen as a trade-off between signal to

noise ratio (which scales with approximately √N (31)) and minimum length of muscle contraction

required to activate the device (too long and it becomes cumbersome and tiring to use). Figure 19

shows the raw signal, filtered signal and RMS smoothed signal for a 3 second isometric muscle

contraction (the y-axis units of these graphs are the output from the analogue to digital converter in

arbitrary units).

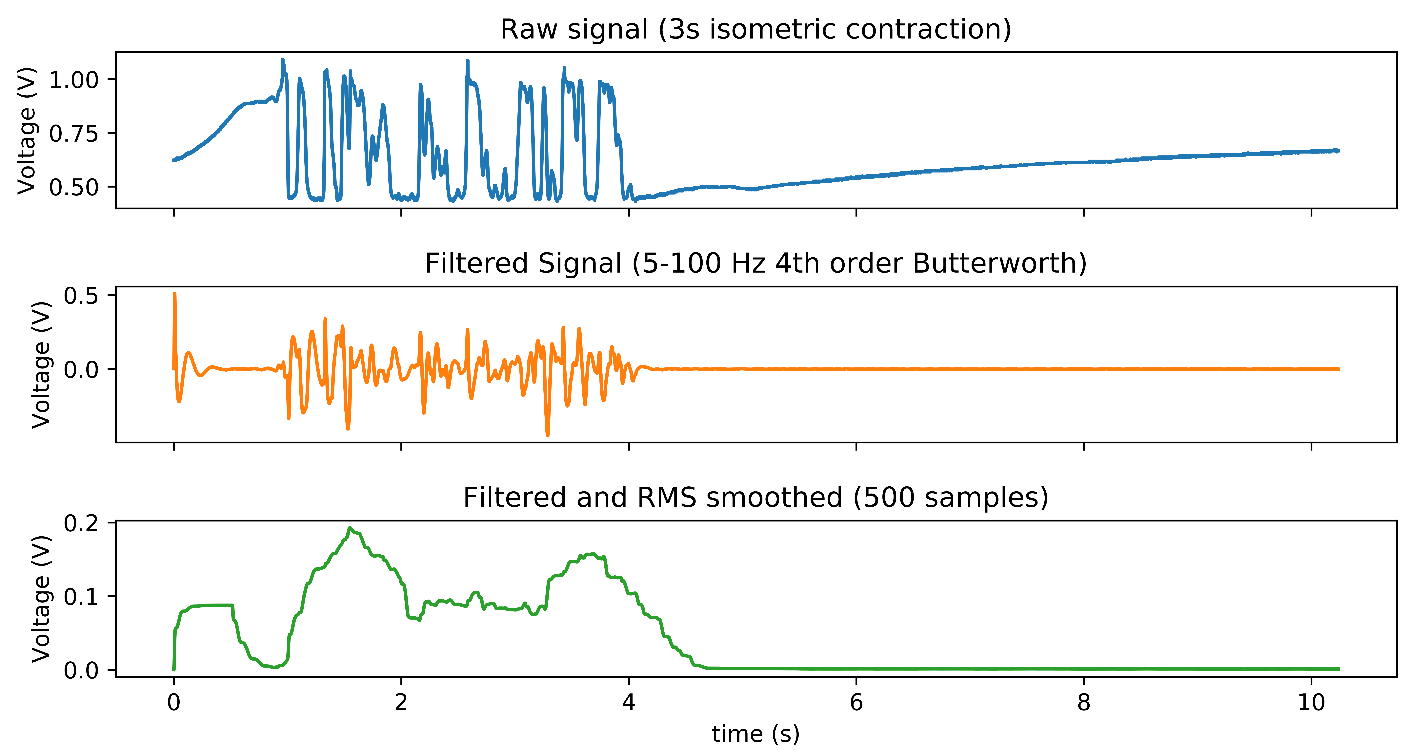
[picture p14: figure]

Figure 19: Signal processing of a 3 second isometric muscle contraction

The signals shown in Figure 19 demonstrate the effectiveness of this signal processing algorithm,

converting a messy raw muscle signal into a simple, smoothed output which is proportional to the

instantaneous power of the muscle contraction.

To classify this smoothed output signal, a simple digital implementation of a Schmitt trigger was

chosen. This is where the muscle is registered as contracted once the smoothed signal rises above an

upper threshold value and the muscle is then registered as relaxed once the signal falls below a

lower threshold value. The separation of upper and lower threshold values prevents the registered

muscle status from oscillating between contracted and relaxed due to noise in the data. For

example, Figure 20 demonstrates the difference between a Schmitt trigger and simple comparator,

using the same muscle data as Figure 19. Clearly, the Schmitt trigger correctly identifies the three

second muscle contraction, whereas the comparator wrongly outputs two short contractions.

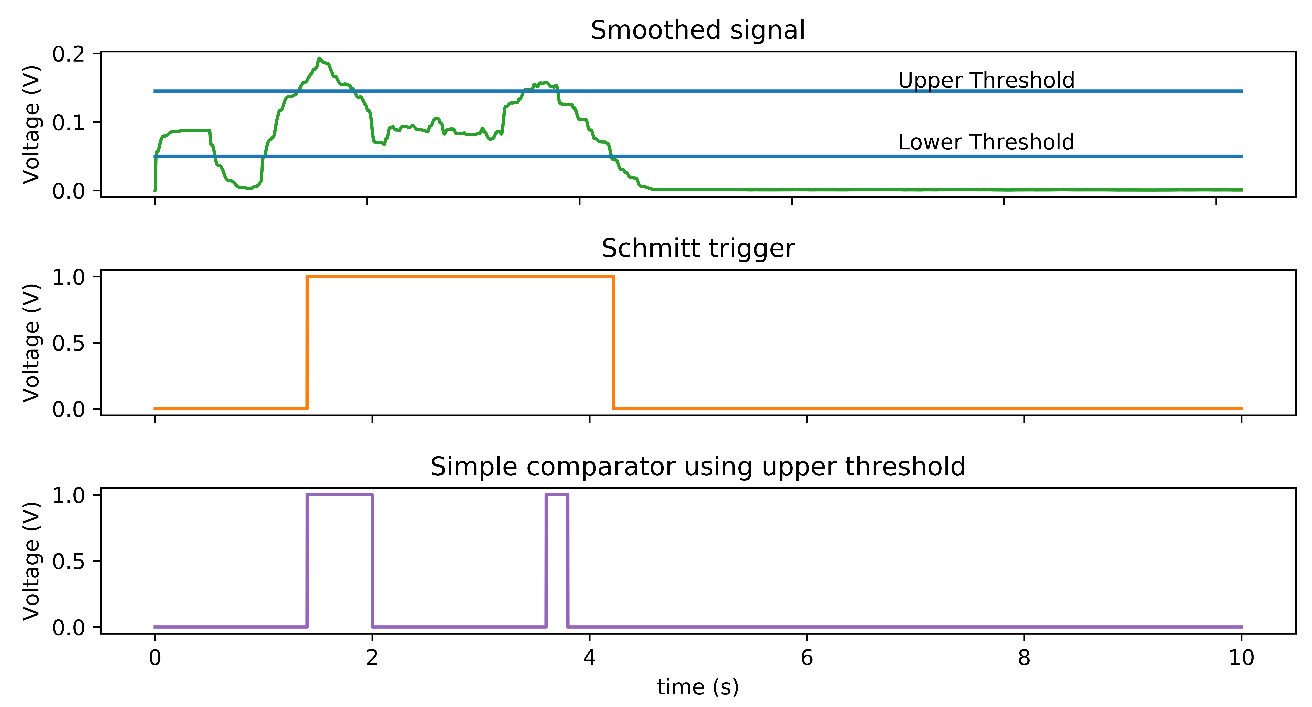
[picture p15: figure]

Figure 20: Comparison of Schmitt trigger against comparator for signal classification

Finally, once the incoming signals from both sensors have been classified to determine whether each

muscle is contracted or not, the prosthesis can decide whether to change grip pose or not. The

details of this are described in sections 3.5.3.1 and 3.5.4.2, where the device operating protocol and

its implementation are discussed respectively.

3.5.3 OPERATING PROTOCOL AND USER EXPERIENCE

This section discusses the operating protocol of the device and user interface features. The three

areas of consideration were: controlling the device in different grip positions, tuning the threshold

value to individual preferences and battery management.

3.5.3.1 MOVING BETWEEN GRIP POSES

The three grip poses of the device are ‘grip’, ‘point’ and ‘open’ and it is important that moving the

prosthesis between these poses is intuitive and easy to learn. The operating protocol involves the

‘point’ and ‘grip’ poses each being associated with one of the muscle sensors. The user can select

one of these grips by simply contracting the relevant muscle and the open pose can be returned to

by contracting that same muscle again. The state transition diagram depicting this protocol is shown

in Figure 21 – in this example, the grip pose is associated with the biceps brachii and the point pose

is associated with the triceps brachii.

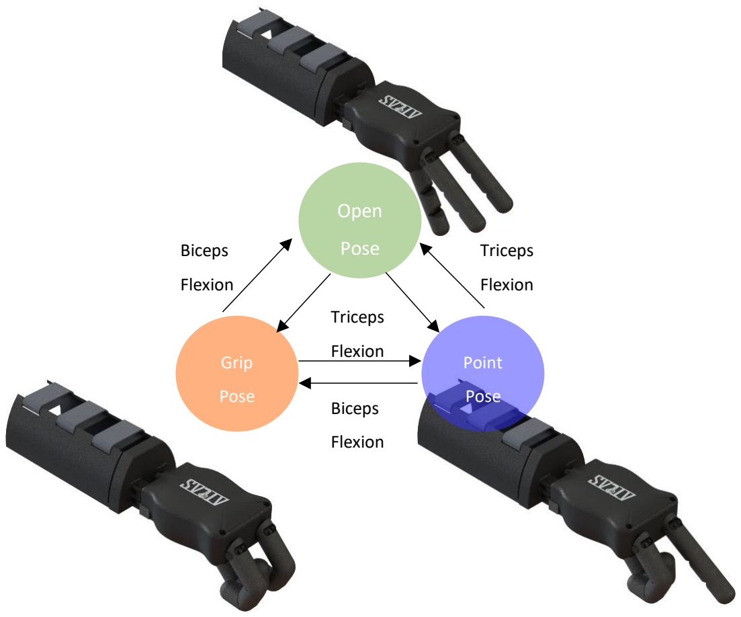
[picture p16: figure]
Open; Pose; Grip; Point; Biceps; Flexion; Triceps

Figure 21: State transition diagram for device poses, showing the working prototype performing each pose

3.5.3.2 TUNING THRESHOLD VALUE FOR INDIVIDUALS

Since this prosthesis must be able to be used by different individuals, the signal classification

algorithm must be able to be slightly changed to suit each user’s physiology and preferences. For this

reason, the upper threshold value for the Schmitt trigger can be altered using a potentiometer inside

the device. When first setting up the prosthesis, each user should start with the potentiometer

turned fully clockwise (representing the highest possible threshold value), then, perform one of the

muscle movements associated with a grip pose (for example biceps flexion) whilst turning the

potentiometer counter-clockwise. Once the device actuates, the user can stop turning the potentiometer and re-attach the cover – the threshold value has now been customised to the

individual. This process was designed to be straightforward and can be performed with one hand by

an amputee – it also only needs to be performed once (when setting up the product for a new user).

3.5.3.3 BATTERY INDICATOR, CHARGING AND SLEEP MODE

Managing battery levels has the potential to be a stressful task for a user who relies on the

prosthesis for daily life. To minimise this, four LEDs and a button are included on the side of the

device (shown in Figure 22). A short press of the button causes the LEDs to light up to display the

device battery level and a long press of the button puts the device into a power saving sleep mode.

While in this mode, a relay inside the device disconnects the motor circuit from the battery and

controller – making it safe to charge using the micro USB port on the side. The prosthetic hand was

designed for people with a transradial amputation on their right arm, so the button and LED

indicators are on the left side of the device for ergonomics.

Figure 22: Rendering of LED and button user interface

3.5.4 SOFTWARE IMPLEMENTATION

The software was implemented in C and a modified version of the Arduino library (32) was used to

provide meaningful names to the pins on the microcontroller and to allow higher level, readable

code without having to focus on the specific architecture and registers of the microcontroller used.

One challenge of this project was implementing the control and UI algorithms to run on a

microcontroller in real time and with low latency; for this to be the case, the main loop of the

program must run faster than the sampling frequency (1kHz). Achieving this involved implementing

the software to be efficient in terms of both space and time – some of the main measures taken

when implementing the code are described here and ‘big O’ notation is used to describe how these

algorithms scale.

3.5.4.1 SIGNAL PROCESSING (MOVING WINDOW RMS CALCULATION)

The moving window involves each sensor having a 500-sample integer array associated with it.

These arrays are the most memory-intensive part of the software and, unfortunately, there is

nothing that can be done about the space requirements as they scale linearly with the size of the

arrays, O(N). However, it is extremely important to ensure that the process of adding and ejecting

data from the queue is as efficient as possible – as well as the calculation of the root mean square. A

snippet of the implementation for these processes is shown in Figure 23.

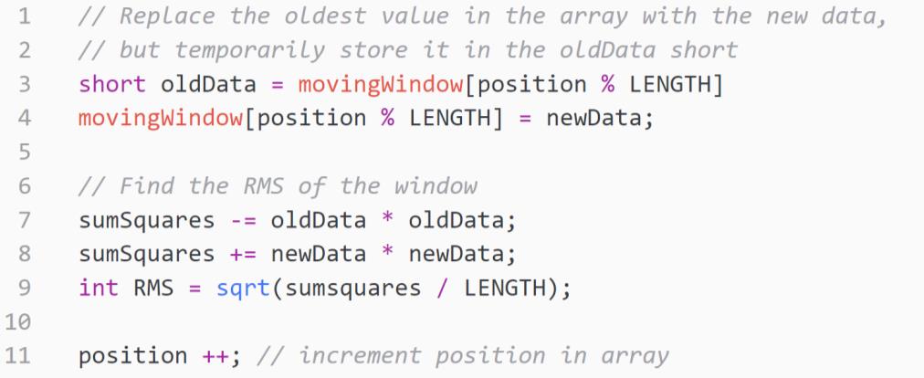
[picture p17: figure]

Figure 23: Efficient implementation of moving window RMS smoothing

This code involves storing the current position in the array and the current sum of the squares of the

array and simply using the modulo operator to make the array circular. Each time new data comes

out of the filter, the oldest value is looked up in the array, stored in a temporary variable and

replaced by the newest value. The new root mean square value is then calculated by simply

subtracting the square of the old value from the sum of the squares running total and adding the

square of the new data to it. The running total is then divided by the size of the moving window and

square rooted to find the RMS value of the window. This code is particularly efficient because it

scales with O(1), meaning that the computational time is constant no matter the size of the moving

window. This helps the program run in real time, where the program must loop faster than the

sampling rate of 1 kHz.

3.5.4.2 SIGNAL CLASSIFICATION

When implementing the signal classification algorithm, computational speed was unlikely to be an

issue because the input data (the processed signal from each muscle) is simply a pair of integers, so

the algorithm does not need to be designed with scale in mind. The most important factor in the

design of this section was code readability and maintainability; for this goal, a state transition table

was the natural choice to use. This is simply an array which takes three inputs: the current pose of the device and the status of the two muscle sensors (either detecting muscle contraction or not). To

classify the muscle signals into a target grip pose, the device simply uses the table to look up which

pose should be activated (shown in Figure 24). The advantage of this method is that the programmer

can easily change the operating protocol by simply changing the numbers in the table – this enables

software updates to be effortlessly and rapidly developed if needed.

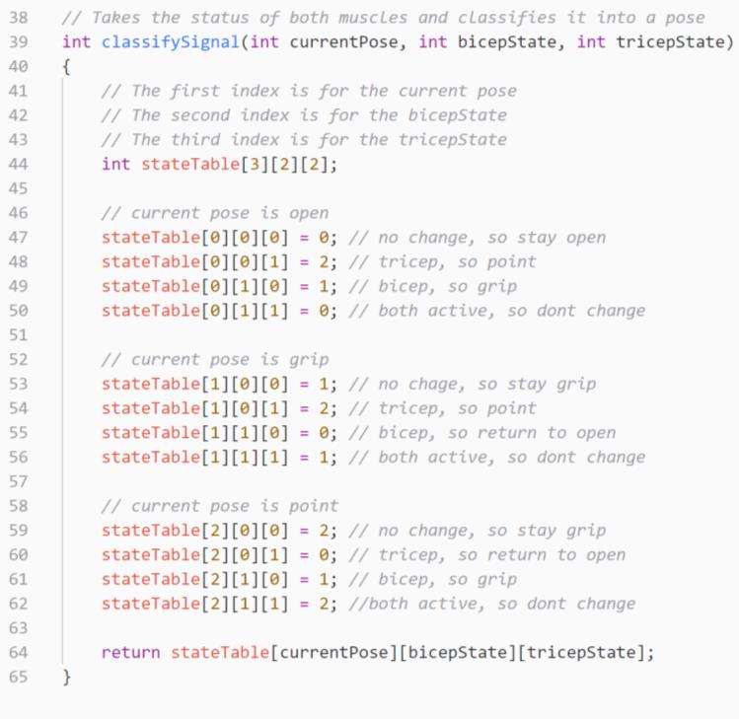
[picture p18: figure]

Figure 24: State transition table for signal classification

3.6 ELECTRONIC DESIGN

To ensure that the product control and power requirements could be met, a key consideration was

the selection of physical electronic components and the designing of a circuit that can allow the full

functionality envisaged in a compact form factor. This section describes the physical electronic

design for the final product and the reasoning behind the design decisions.

3.6.1 MECHANOMYOGRAPHIC SENSORS

Due to the nature of MMG muscle signals as low-frequency vibrations, many commercial

microphones are capable of picking up these signals. Fortunately, however, SERG technologies (a

spin-off company from Imperial’s Biomechatronics laboratory) kindly gave us three sensors they had

developed for commercial use. These sensors consist of a Knowles SPU1410LR5H-QB MEMS

microphone, housed in a 3-D printed casing – shown in Figure 25. The shape of the casing directly

affects the quality of the signals acquired and the optimal shape was found by Posatskiy and Chau

(33). These sensors were more than suitable for this project, so development of our own sensing

unit was not necessary.

Figure 25: MMG sensing unit configuration, adapted from figure 1 of (34).

3.6.2 CONTROLLER

Selecting an appropriate microcontroller was the centrepiece of the electronic circuit design, with

several requirements such as memory, clock speed and input / output (I/O) factoring into the final

choice. Another consideration was whether to purchase a standalone controller and develop our

own printed circuit board (PCB) to fit the electronics or to purchase a general-purpose development

board, such as those made popular by Arduino in recent years. It was decided early on in the project

that the latter approach would be more suitable because the design and manufacture of a suitable

PCB would be a significant drain on the project’s time and resources, with comparatively few

benefits compared to using an ‘off-the-shelf’ solution.

When selecting the microcontroller, it was vital to select one with sufficient memory and clock

speed to run the taxing signal processing code in real time. Early testing made use of an Arduino

UNO board, which contains an 8-bit controller with 32 kB of flash memory and a 16 MHz clock

speed, however, it quickly became apparent that this board lacked the required memory and speed

to run the code when two sensors were used. After careful consideration, the Adafruit feather M0

Basic board was selected – this contains a 32-bit microcontroller with 256 kB of flash memory and a

clock speed of 48 MHz, providing several benefits over the less powerful Arduino. The Adafruit board

is fast enough to process the data from both sensors in real time and also has enough memory to

easily hold the 500-sample moving window (described in section 3.5.2) in working memory, where

the Arduino could only hold a maximum of 100-samples. Other advantages of this board are the

inbuilt battery management and charging systems as well as a low-power sleep mode; this enabled

user experience features such as a standby mode and an easily accessible micro USB charging port to

be easily integrated into the product.

3.6.3 MOTORS

The final concept, developed following the morphological analysis outlined in section 3.3.3,

identified linear motors as the primary actuation method. Maximum force and power requirements

were the main factors considered when choosing motors as they must be capable of meeting the

grip strength requirement set out in the PDS, whilst not demanding a large battery. Stroke length

was also important because the motors must be able to pull the fingers through their full range of

motion, without being bulky or heavy. These strict requirements limited the scope of selection

significantly, with the Actuonix PQ-12 linear servo motors standing out as the natural choice for this

project. Each PQ-12 can provide a maximum force of 50 N, consumes approximately 3 W when

stalled and has a stroke length of 20 mm; these motors lie on the premium end of the spectrum

(costing a minimum of £ 85 per motor), however, discussions with experts in the field such as Alex

Lewis and our supervisor Dr Ravi Vaidyanathan justified this expense as they emphasised the

importance of strong, reliable grasping in prosthetic hands. Figure 26 shows the motors in use in a

functional prototype of the device.

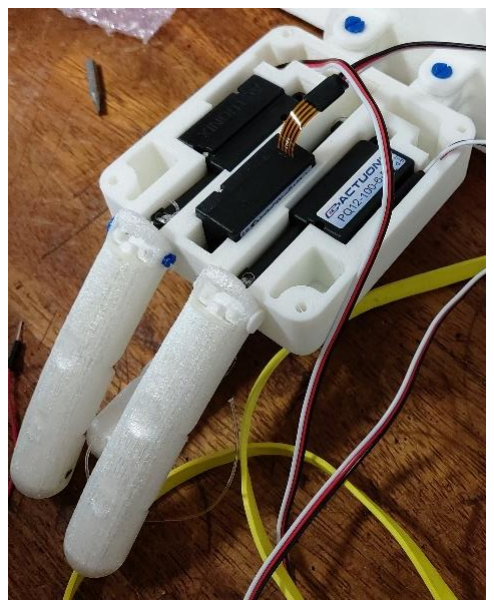
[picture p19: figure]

Figure 26: Actuonix PQ12 motors displayed in working prototype

3.6.4 POWER SUPPLY AND CHARGING

3.6.4.1 BATTERY SELECTION

Battery selection involved balancing capacity, discharge current, voltage and size. These design

parameters are each crucial and required careful calculation to ensure that the best battery was

chosen. The most compact batteries available were 3.7 V LiPo batteries, which are ideal for

powering the Adafruit 3.3 V board – one slight complication though is that the PQ-12 motors require

a 6 V voltage source. This was easily solved by the inclusion of a ‘buck-boost’ DC-DC voltage converter to step up the voltage which, naturally, increases the current draw of the motors by 74 %,

due to conservation of energy (P = IV) and inefficiencies in the converter. This high current draw

meant that the battery had to be selected with a large enough capacity to operate with the battery

life specified in the PDS and to withstand the maximum current draw of the motors under maximum

load. The minimum necessary capacity was calculated using | Equation 2, using the

parameters listed in Table 7.

Table 7: Parameters used in battery calculations

Parameter Physical Meaning | Value | Justification (where necessary)
Nm | Number of motors | 3
im | Current draw of one motor during an operation | 0.25 A | Experimental evaluation of motor current using ammeter
Nops | Number of operations per hour | 60 | Heavy use will average out to one operation per minute
Tlife | Battery life | 12 h | Minimum battery life specified in PDS
Vmotor Vbattery | Current magnification caused by boost converter | 1.622 | Simply divide output voltage (6 V) by input (3.7 V)
ηboost | Efficiency of boost converter | 0.93 | Specified in converter datasheet
ic | Current draw of microcontroller | 0.05 A | Experimental evaluation of current draw using ammeter
top | Time taken per motor operation | 3
| | 3600
| | h | Each motor operation takes approximately 3 seconds

NmimNops top Tlife

Vmotor

Vbattery

ηboost + Tlifei
c
= Minimum capacity (Aℎ) | Equation 2

The minimum battery capacity required was calculated as 1.49 Ah. Due to the need for a reasonable

safety factor on battery life, the battery chosen was a 3.7 V, 2Ah LiPo – capable of delivering 2 A

under continuous discharge.

3.6.4.2 ISOLATING RELAY

When the device is in sleep mode, it is important that the motors are electrically separated from the

battery to prevent constant unnecessary current draw (and to prevent backflow whilst charging). It

was decided to do this using a latching relay, which can be toggled by the microcontroller when the

user pushes the power button. Fortunately, Adafruit produce an ‘off-the-shelf’ solution to this

problem in the form of a latching relay board which simply stacks on top of the microcontroller

board – the ‘FeatherWing relay’. This provided a compact and elegant solution to the problem of

isolating the motor circuit (depicted in Figure 27) and was superior to a mechanical switch because it

does not add any complexity to the user interface or operating protocol.

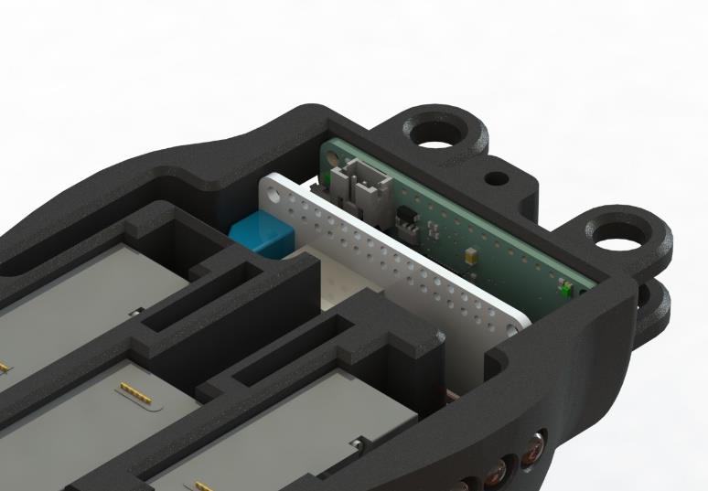
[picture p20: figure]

Figure 27: Rendering of Adafruit feather microcontroller board and FeatherWing relay in the final product

3.6.5 OVERALL CIRCUIT

The full circuit diagram is shown below in Figure 28. This is a demonstrative simplified version rather

than a full layout drawing. For example, the FeatherWing latching relay contains a number of inbuilt

transistors and logic gates as drivers for the relay, but these are not shown on the below diagram for

simplicity.

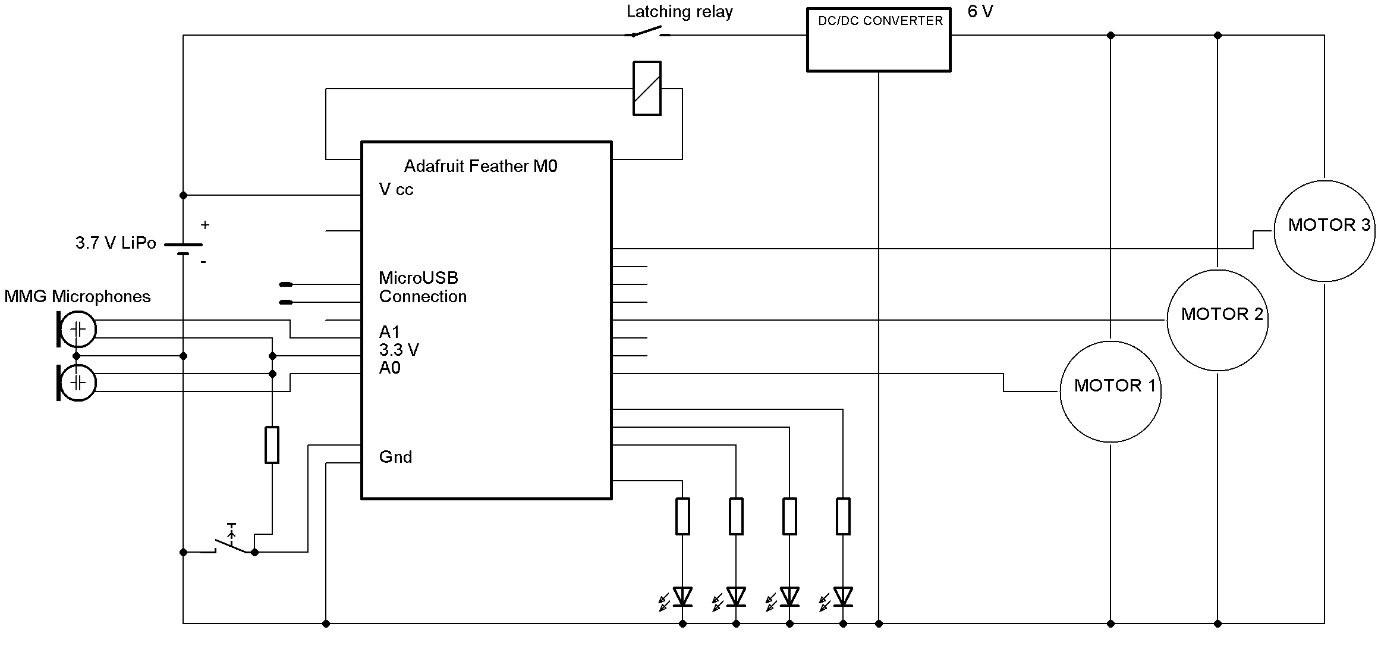
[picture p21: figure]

Figure 28: Demonstrative circuit diagram of electronic system

3.7 FINAL DESIGN

The figure below shows the final prototype produced, the ATLAS Arm, on a display stand and

mounted to a plaster of Paris arm cast. The final prototype consists of TPU-PLA composite fingers, a

smoothed hand section with feature integration such as LED battery level indicators and a button-

operated sleep mode, the logo printed into the cover, a moulded wrist unit and an MMG sensor

strap. The assembly and manufacture of the final prototype is detailed in section 4.

Figure 29: Final product on display

4 MANUFACTURE AND ASSEMBLY

Having discussed the overall design of the product, it is important to now look at the manufacturing

and assembly. A large amount of this work was done in parallel with the design process, as our

chosen manufacturing method of 3-D printing had a large impact on design. In this section we will

cover the reasoning behind our choices of manufacturing method and material selection. We will

also cover the assembly details for both the electronics and the mechanical hand.

4.1 METHODS AND JUSTIFICATION

Fundamental to the project from the beginning was the desire for the product to be manufactured

in a decentralised fashion. This limited the range of manufacturing methods to those reasonably

available to engineers and hobbyists who might volunteer to make the prosthesis for a local

amputee. Although some methods (such as laser cutting) can be used to manufacture parts

accurately for low cost, they are often relatively inaccessible, especially in developing countries –

making them unsuitable for this project. Desktop 3-D printers are fast becoming the manufacturing

method of choice for makers on a budget and, with an estimated 500 000 desktop printers sold in

2018 (35), 3-D printing stood out from the beginning as an important manufacturing method to

utilise. In fact, an organisation, E-NABLE, already exists to connect amputees with local volunteers

who can 3-D print open sourced body-powered prosthetic designs (36). Another advantage of 3-D

printing is the speed and low-cost for small- batch production, typically considered best-in-class for

polymers; repairs and replacements are also accelerated, with end users simply able to print

replacement parts instead of sending the entire device into a central facility for repair.

There are many different types of 3-D printers, with the most prevalent being fused deposition

modelling (FDM) printers, however, all 3-D printers follow the same basic principle. First a CAD file is

put into a slicer software which takes the model, cuts it into layers and writes code which is inputted

into the printer. The printer then constructs the model layer by layer. In FDM printers the layers are

printed by extruding a “string” of plastic, as shown in Figure 30.

Figure 30: Fused deposition modelling. Image from 3DInsider (37).

All parts manufactured in this project were produced on one of the group’s two Creality Ender 3

machines; this is one of the most popular commercial 3-D printers available and can be purchased

for the entry level price of £ 150, making it a reasonable assumption that any hobbyists making our

product will have a machine of similar quality. One feature this printer boasts is a heated print bed.

This feature is extremely useful in preventing warping, which occurs when the temperature gradient

across the part is too large and results in sections contracting at different rates, deforming the

printed part. It is therefore advantageous to have a heated bed as it will result in more accurate

parts. Although this feature is not present on all printers, most modern printers (such as the Ender 3)

generally have this as standard.

4.2 MECHANICAL CHARACTERISTICS OF FDM PRINTED PARTS

There are inherent structural and mechanical issues with FDM parts, which can often dissuade

engineers from selecting this as a primary manufacturing process. Some of these problems include:

| • The extruded filament bonding poorly to the already partially cooled polymer layer below
| (poor layer adhesion).
| • Gaps occurring between extruded filaments.
| • Rough surface finish due to the layered nature of construction.
| • Anisotropic material properties, such as weakness in the direction perpendicular to layers.

These limitations can be mitigated through careful design of mechanical parts and experience in

selecting optimum print settings. The following section (4.3, design for 3-D printing) explores many

of the manufacturing-specific decisions made during this project, including tests which were

performed to provide evidence for them. Testing (detailed in section 6) was also performed on

prototype parts to ensure that these potentially negative characteristics did not affect the product’s

ability to perform according to the PDS.

4.3 DESIGN FOR 3-D PRINTING

Having selected FDM 3-D printing as the primary manufacturing method for this project, it was

crucial to ensure that all parts were designed with this manufacturing method in mind. This section

summarises the design decisions and iteration that occurred as part of this design for manufacture

philosophy.

4.3.1 PRINT ORIENTATION

It is a well-known fact that 3-D printed components are anisotropic in that they have different

material properties depending on the orientation the part is loaded in. Therefore, an experiment

was done to assess the strength of printing in the different orientations with the materials selected.

4.3.1.1 TESTING METHOD

In this experiment, six specimens with dimensions 5 x 20 x 60 mm were printed in both PET-G and

PLA (two printed in each orientation). The specimens were then clamped in an Instron tension and

compression machine with a 24.75 mm gap between the clamps. They were then pulled at a rate of 5 mm min⁻¹
and the displacement and load were recorded over time. The specimen was pulled until

the load dropped by 60 %, which occurred after rapid brittle fracture. The load and displacement

were then converted into stress and strains using Equation 3. Strain against stress graph were

plotted, and the Young’s Modulus was then given by the gradient of the linear section of the graph

(before significant plastic deformation occurred). The moduli for each orientation were then

averaged. The ultimate tensile stress (UTS) and the engineering stress that the specimen reached

before fracture were also found.

Stress =

Force
Cross Sectional Area

, Strain =

Displacement
Exposed Lengtℎ

Equation 3

4.3.1.2 TESTING RESULTS

The results of the experiment are found below in Table 8. The data shows that although the

difference in Young’s Modulus is small, there is a larger difference in the ultimate tensile strength,

with the strongest orientation being involving printing along the axis of the thin but long edge and

the weakest being printing along the axis of the short thin edge. The reasoning behind this is

complex. When pulling the specimen printed on the short thin face the layers are getting pulled

apart, whereas in the other two orientations the fibres are in tension, rather than the bonds

between the layers. This implies that interlayer adhesion is the key variable in the strength of the

print. The difference between the other two orientations will therefore also be due to the inter layer

adhesion. Since the layers printed along the thinner edge are printed quicker, they are warmer when

the second layer is added, meaning interlayer adhesion is better, explaining the observed results.

Thus, it was found that it was most important to avoid printing in an orientation that would mean

the load applied would be perpendicular to printing plane. With secondary importance, it would also

be important to try and print in an orientation that would mean smaller layer area, so that each

layer printed quicker and therefore the interlayer adhesion would be higher.

Table 8: Results of Print Orientation Experimentation

Material Face on Build Plate | UTS (MPa) +/- | E (GPa) +/-
PETG | Fat Face (20x60mm) | 20.851 | 3.103 | 0.455 | 0.022
| Thin Long Face (5x60mm) | 35.576 | 2.027 | 0.529 | 0.044
| Thin Short Face (5x20mm) | 10.696 | 4.647 | 0.496 | 0.064
PLA | Fat Face (20x60mm) | 22.299 | 14.465 | 0.497 | 0.213
| Thin Long Face (5x60mm) | 25.695 | 10.111 | 0.535 | 0.119
| Thin Short Face (5x20mm) | 9.557 | 1.200 | 0.584 | 0.081

4.3.2 SIZING AND TOLERANCES

A second issue that arises with 3-D printing is that tolerances cannot be applied to the printer as it is

printing. The slicing software will take the ‘perfect’ CAD model and write code to make the printer

print to the exact nominal dimensions of the model. The printer itself is not perfect and therefore

the print will not have the exact dimensions of the model. This is compounded by factors such as

shrinkage where, as the deposited polymer cools, the polymer becomes less amorphous and more

crystalline – increasing the density and reducing the volume of that section of the part. Due to the

low thermal conductivity of polymers, and relatively high print temperatures, shrinkage is

aggravated in thicker parts as the centre of the part cools slower than it would near the surface,

allowing greater time for chain re-alignment and resulting in higher crystallinity. These factors can

cause problems when printing parts with tight tolerances, so two methods were used to mitigate

against them.

Firstly, parts with important tolerances were printed with a variety of slightly differing nominal sizes,

this allowed them to be tested experimentally to determine the quality and consistency of the fit.

The second method involved, where possible, designing regions with tight tolerances to dissipate

heat during printing – hence reducing the effect of shrinkage on that region of the print. This is

demonstrated in Figure 31, which shows the connectors which attach the palm to the socket. The

high surface area of these connectors was intentionally designed to allow them to act as thermal

fins, dissipating heat and preventing warping which might affect the fit.

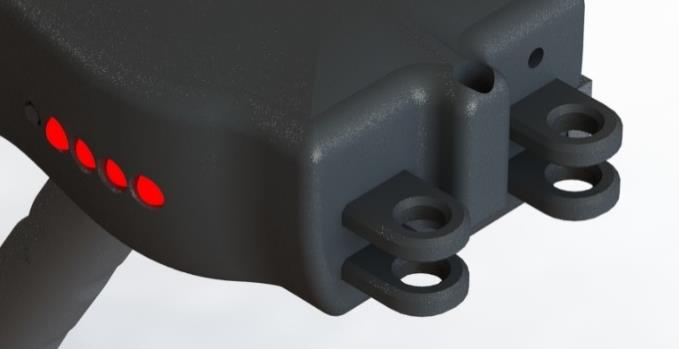
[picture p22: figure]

Figure 31: Rendering of palm connector points

4.3.3 SUPPORTS

An area which majorly impacts print quality is support structure. This is something unique to 3-D

printing due to the layer by layer construction and is necessary when the part contains large

overhangs or bridges. Printers tend to struggle when printing on thin air for significant distances,

causing the resultant structure to sag or the print to fail entirely. Support structure is therefore

essential for these overhangs; however, minimising support structure is typically a good idea to

reduce material consumption and limit the amount of necessary post-processing. To minimise the

necessary supports, parts were printed in the orientation which leads to the fewest overhangs

(provided the print orientation did not create structural weak points). Parts were also designed in

such a way to minimise support structures, a skill we improved at considerably throughout the

project. Figure 32 shows two iterations of the socket design, with support structure depicted in

green. The second design (B) was made with the goal of reducing support material explicitly, after it

was discovered that the support material on first design (A) was difficult to remove, leaving plastic

sprues (residue) which worsened the finish. Design B required only 31 % as much support material as

A, was faster to print and had a better surface finish.

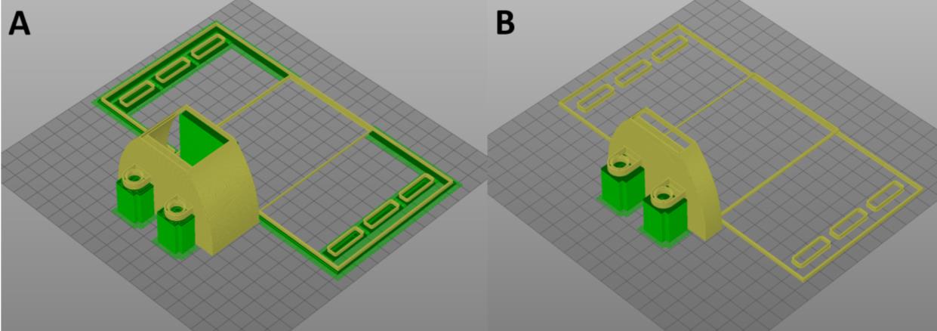
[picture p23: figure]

Figure 32: First iteration of socket design (A) and socket after being redesigned to minimise support material (B).

4.4 PRINTING WITH PETG, PLA AND TPU

A common misconception is that changing material on an FDM printer is as simple as just changing

the print temperatures. Due to the different properties of each material, there are many different

settings that had to be tuned to ensure the prints were successful and did not suffer from

mechanical problems. This involved lengthy research and experimentation, combined with

experience to get the settings right.

PLA is the simplest material to print with, hence a reel of it is normally delivered with any new 3-D

printer. The optimal print settings for this material are well known so this material required little

work to produce good results.

PETG is a less commonly used material and although there is a large amount of information about

printing with it, differences in PETG composition between manufacturers (combined with

differences in commercial printers) made it difficult to initially produce ideal results. After several

rounds of trial and error, we found that with PETG produced by eSUN, the filament printed best with nozzle temperature of 210 oC and build plate temperature of 100 oC.

TPU was the hardest material to print in due to its flexibility, as it would easily buckle while being fed

into the nozzle and therefore result in under-extrusion. Another issue was that support structures

were extremely difficult to remove due to the flexibility of the material. The final issue was that

parts that were tall in the z-axis flexed and bent during printing, meaning filament was extruded

onto the parts in the wrong place. These issues were corrected by lowering the print speed

significantly, orienting parts so they have a large build base and increasing the gap between support

structures and the actual part. PVA glue was also applied to the build plate to improve first layer

adhesion.

A summary of the key printer settings can be seen below in Table 9.

Table 9: Printer Settings for the different materials

| PLA | PETG | TPU
Print Speed (mm/s) | 30 | 30 | 8
Print Temperature (oC) | 180 | 210 | 200
Bed Temperature (oC) | 60 | 100 | 30
Extra Adhesive on Plate? | None | None | PVA glue

4.5 ASSEMBLY OF ELECTRONICS

Assembly of the electronics in the final product was designed to be simple, with electronic

components being wired together outside of the casing and simply lowered into place. The wires

would be soldered into place and heat shrink sleeves would be wrapped over any exposed wire to

provide electrical isolation for user safety and to remove the possibility of any short circuits.

Unfortunately, due to the college shutdown, assembly of electronic components in the final product

was unable to be completed (a topic further discussed in section 7.1, the effect of college shutdown

on this project); although we estimate that an individual with soldering experience would be able to

complete this process in under two hours. Figure 33 shows the positioning of the electronics in the

final product.

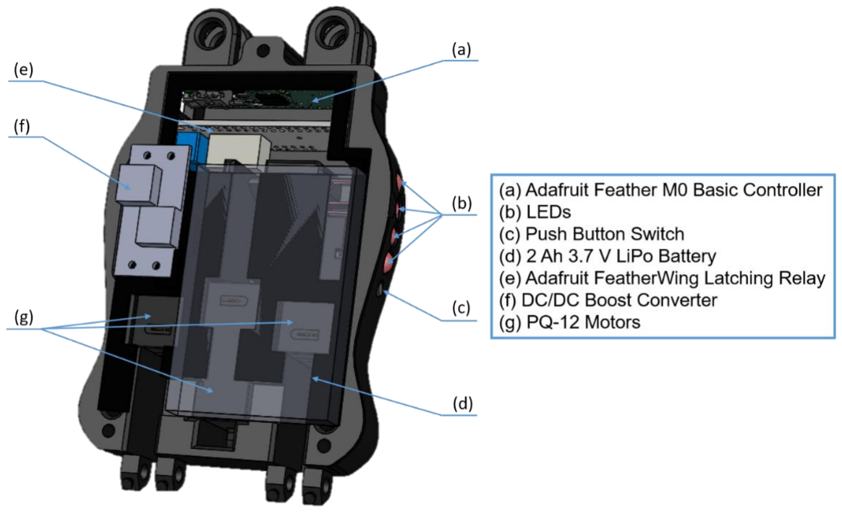
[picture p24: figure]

Figure 33: Electronics Layout

4.6 OVERALL ASSEMBLY

The overall assembly of the prosthesis, shown in the assembly drawing on the following page, is a

four stage process: first assemble the electronics as in Figure 33; then assemble the three finger

subassemblies; attach the finger subassemblies to the palm, threading the fishing wires through to

the motors; and finally attach the socket to the palm. Once that has been complete, simply screw

the cover onto the palm with three M3 bolts and the product is fully assembled.

5 PRODUCT COST AND BUDGET

This section briefly assesses the budget of the project and the cost of the final product. It was of

upmost importance during the project to not run over budget and the cost of the final product is a

key factor when determining the success of our product.

5.1 FINANCE AND BUDGETS

By producing a working prototype and performing design verification tests, some of the £ 1000

project budget was used for purchasing materials which were not used in the final product. This was

planned for from the beginning of the project and careful project management ensured the project

did not run over budget. Table 10 shows a breakdown of the total costs planned and the actual

expenditure. The PQ-12 motors were responsible for budget in the motors/sensor category being

exceeded; this was due to the motors being purchased from an ICIS approved supplier at a

significantly higher price than they are obtainable for on the open market. The overall budget for the

project, however, remained below the planned budget due to planning and accounting for this risk.

In total, only £ 575 of the total budget was spent, making this project successful and cost efficient.

Table 10: Breakdown of Budget

Budget Breakdown: | Allocation: Expenditure:
Motors / Actuators / Sensors | £250.00 | £342.57
Various Materials | £150.00 | £47.41
Plastic Filament | £100.00 | £117.49
Other Electronics | £100.00 | £67.50
Total: | £600.00 | £574.97
5.2 | FINAL PRODUCT COST

Table 11 shows the exact cost to manufacture the final prototype by summing the cost of all

purchased and manufactured components. This was £ 399.02, however, if purchasing the product

through non-ICIS suppliers, significant savings could be made by procuring the PQ-12 motors for far

cheaper – bringing the total cost down to £ 238.73. The manufacturing methods necessary are also

low cost, with only a budget 3-D printer (around £ 150) and a soldering station (around £ 10)

required to manufacture the product.

Table 11: Final prototype cost

Product Name / Descriptor & (Purchaser)

| Supplier | Unit Cost (incl. shipping) | Quantity / Portion of

Packet

| | | | Total Cost | Budget Category
Actuonix PQ12 Micro Linear Actuator, 20% Duty Cycle, 6V dc, 10mm/s, 20mm | RS - Online | £113.03 | 3 | £339.0
| | | | 9 | Motors / Actuators / Sensors
Straps | Amazon | £7.95 | 0.5 | £3.98 | Various Materials
JST-PH Wire Assembly | Pimoroni | £3.59 | 0.1 | £0.36 | Various Materials
Wide Black Elastic Band | Amazon | £4.99 | 0.1 | £0.50 | Various Materials
Eventronic ET 1002 Heat Shrink Tubing Electric Insulation Heat Shrink Wrap Cable Sleeve 5 colours | Amazon | £5.99 | 0.1 | £0.60 | Various Materials
RS PRO 3.7V, Lithium Polymer Rechargeable Battery, 2 Ah | RS - Online | £17.70 | 1 | £17.70 | Other Electronics
LATEX FREE BRACES Elastic Orthodontic Bands | Ebay | £2.99 | 0.1 | £0.30 | Various Materials
ADAFRUIT Feather Cortex-M0 Proto Board | RS | £15.21 | 1 | £15.21 | Other Electronics
FeaterWing Latching Mini Relay Board | RS | £6.07 | 1 | £6.07 | Other Electronics
Short Feather Headers Kit 12-pin and 16-pin Female Header Set | Pimoroni | £4.49 | 1 | £4.49 | Other Electronics
All Printed Components | | - | - | £10.73 | Plastic Filament
| | | Total Cost | £399.0
| | | | 2

6 TESTING AND DESIGN VERIFICATION

The third main component of this design, make and test project is, naturally, testing. This is a crucial

part of the process, where the manufactured product is examined to discover if it meets the criteria

specified in the PDS. As part of our iterative design process, many tests were performed at all stages

of the project to inform design decisions, however, this section will only focus on the final tests

performed to verify the product against the PDS.

6.1 DESTRUCTIVE TESTING

Destructive testing was performed, focussing on the mechanical strength of the product. Three tests

were planned: a 3-point bent test to verify the maximum load; an impact test to evaluate toughness

and robustness of the product; and a fatigue test to ensure the lifetime is not limited by fatigue

issues.

6.1.1 3-POINT BEND

6.1.1.1 INTRODUCTION

As specified in section 4.3.1, 3-D printed components are anisotropic, meaning each component had

different material properties and failure points according to its print orientation. To test the design,

the stress and failure points needed to be quantitively assessed using destructive testing. Therefore,

an experiment was done to assess the strength of the device, specified in the PDS as minimum 50 N,

and determine the failure criteria.

6.1.1.2 METHODS AND DATA

In this experiment, three test samples of the working prototype were printed in PLA and placed onto

a 3-point bend workpiece holding in an Instron tension and compression machine. The purpose was

to test the strength of the connecting pins between the hand and the wrist and find the maximum

theoretical load that the hand could hold, in order to verify the PDS condition of withstanding a 50 N

load. There was a 35 mm distance from the centre to each support, and machine extended at a rate

of 1 mm/s. The setup is demonstrated in Figure 34. The time, displacement and load were recorded.

The specimen was compressed until the load dropped by 60%, which occurred after the specimen

fractured. The data was analysed to find the maximum force applied before fracture, and the

component visually inspected to find the point of failure. Using the maximum force applied, the

maximum load applied to the end of the hand can be calculated by doing a force balance, then

finding the resulting moment about the whole hand unit, given by Equation 4.

Max Load for Hand =

Force Applied
2

×

distance to pivot
distance to end of ℎand

=

Fa
2

×

0.0035
0.0075
Equation 4

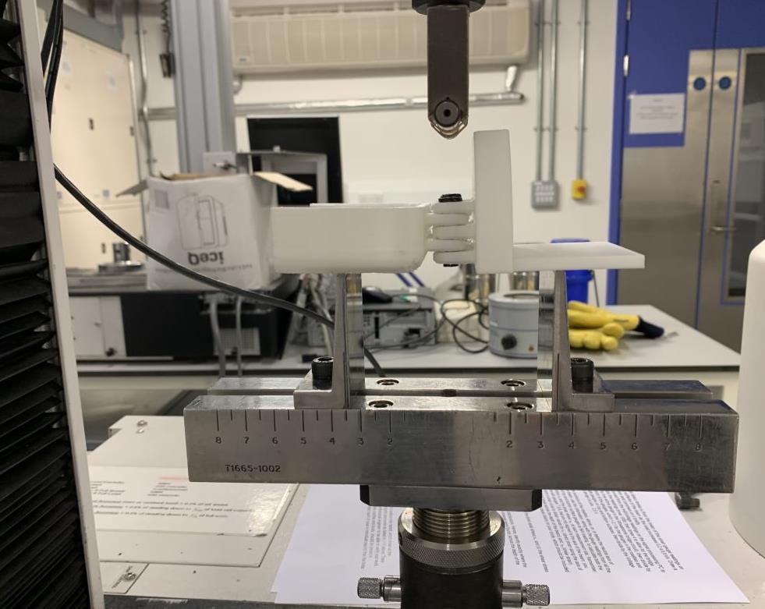
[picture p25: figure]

Figure 34 - 3-point bend set up

6.1.1.3 RESULTS

The results of this experiment are found below in Table 12.

Table 12: 3-point bend test results

Sample | Max Force Applied
| (N) | Max Load of whole
| | hand (N)

Picture Failure

Mechanism

1 | 336.7 | 78.6
2 | 570.6 | 133

3 | 524.8 | 122
Average | 477.4 | 111 | Layer separation

6.1.1.4 DISCUSSION

This data shows that the point of fracture of each sample was not the connecting pins between the

hand and the wrist; the failure was layer separation, demonstrating that the connecting pins are

strong enough to connect the two sections.

Moreover, the average maximum theoretical load that can be applied to the whole hand is 111 N,

which is higher than the specified minimum load to failure of 50 N in the PDS. Thus, the test can be

considered a success, and validates the stated PDS criterion.

6.1.2 IMPACT TEST

To test the durability of the design a simple drop test was conducted. In this experiment the whole

product was dropped from gradually increasing heights until a fracture occurred. The aim of this

experiment was to ensure that the device would be resistant to being knocked, dropped and hit; this

is important because many low cost designs do not have the durability and toughness to survive day

to day usage. The results found that the maximum height the product could be dropped from is 2

metres and the failure mechanism was a fracture on the thumb connecting point, pictured in Figure
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

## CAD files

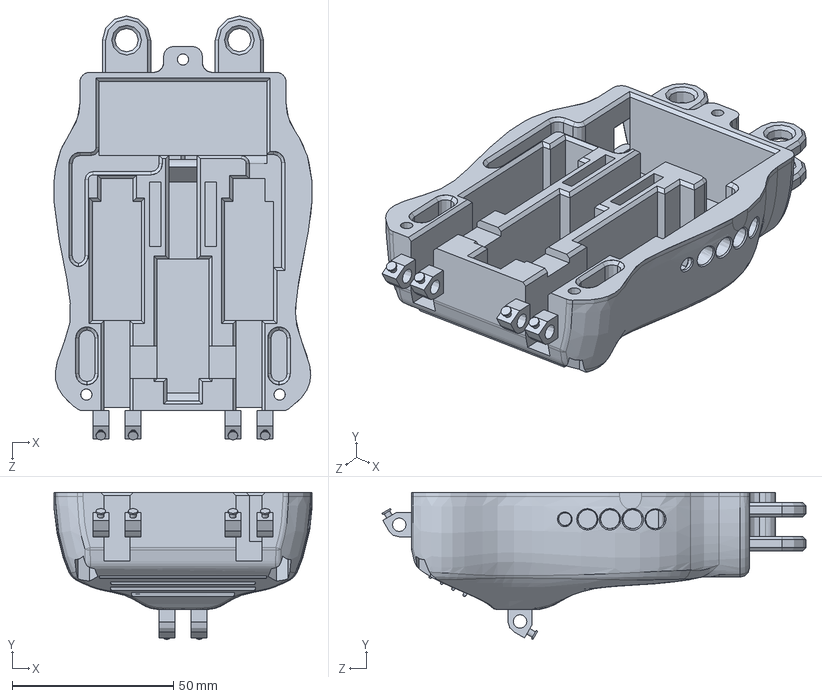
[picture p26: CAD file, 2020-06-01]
Hardware/SOLIDWORKS FILES/HAND MAIN V10.SLDPRT
80.0 x 45.7 x 131.6 mm

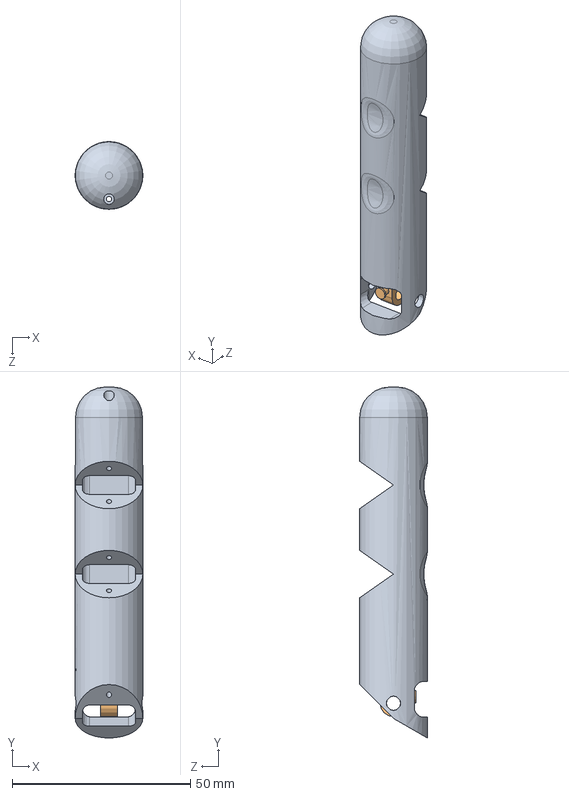
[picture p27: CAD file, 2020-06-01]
Hardware/SOLIDWORKS FILES/FINGER ASSEMBLY v3.SLDASM
19.0 x 98.5 x 19.0 mm
FLEXIFINGER v4
PHALANGE 1 v4
PHALANGE 2 v4
PHALANGE 3 v4

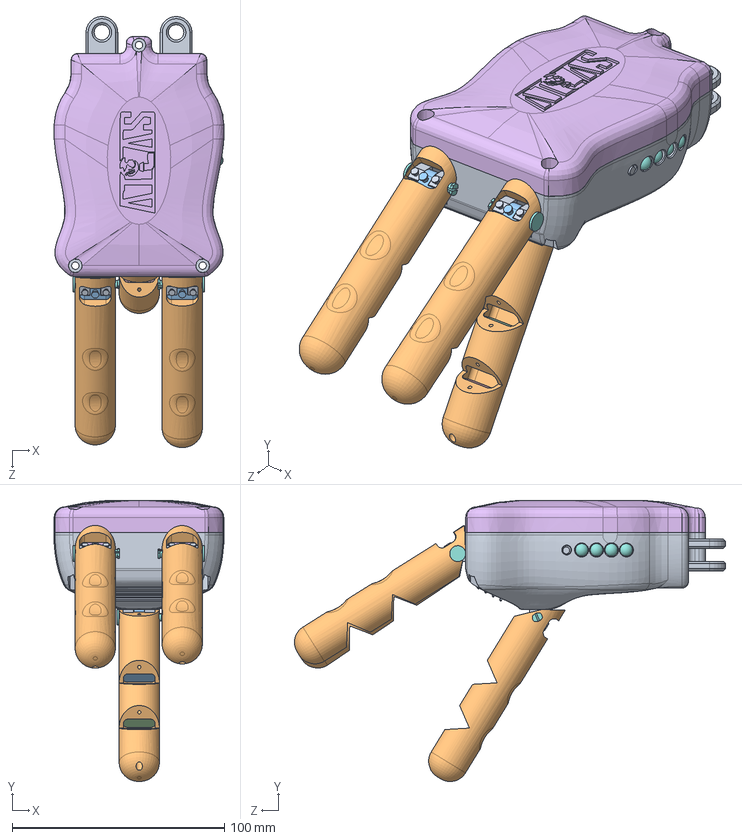
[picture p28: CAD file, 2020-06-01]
Hardware/SOLIDWORKS FILES/Assembly v6.SLDASM
80.0 x 132.5 x 203.2 mm
HAND MAIN V10
FLEXIFINGER v4 x 3
PHALANGE 1 v4 x 3
PHALANGE 2 v4 x 3
PHALANGE 3 v4 x 3
COVER v5
Battery v1
LED v1 x 4
Switch v1
Adafruit Relay
Board.step
10uF.step x 4
1k.step x 15
GREEN.step x 4
SPST_TACT-KMR2.step
microUSB.step
MCP73831T-2ACI_OT.step x 2
MBR120.step
JSTPH.step
ATSAMD21G18_QFN.step
32.768.step
Actuonix PQ12-100-12-P-Housing x 3
Actuonix PQ12-100-12-P-Shaft x 3
pin knuckle x 3
Mid Plate
DCDC Boost

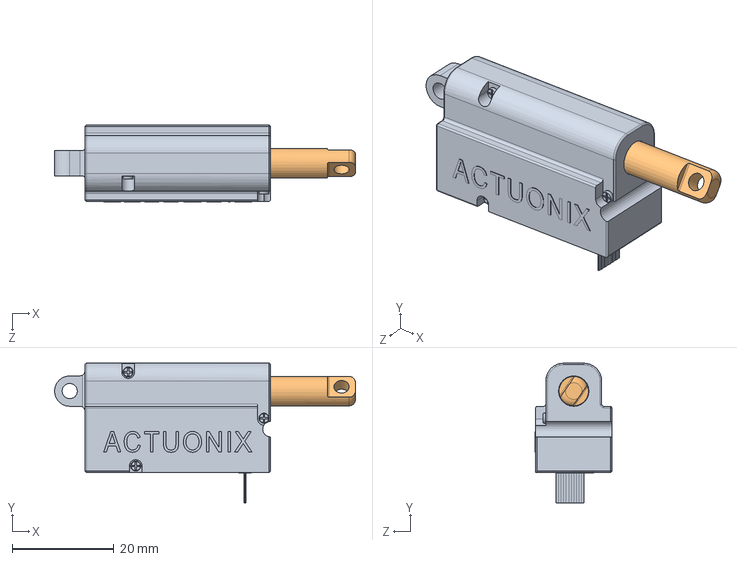
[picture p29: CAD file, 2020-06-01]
Hardware/SOLIDWORKS FILES/PQ12 Ass.SLDASM
59.3 x 27.5 x 15.1 mm
Actuonix PQ12-100-12-P-Housing
Actuonix PQ12-100-12-P-Shaft

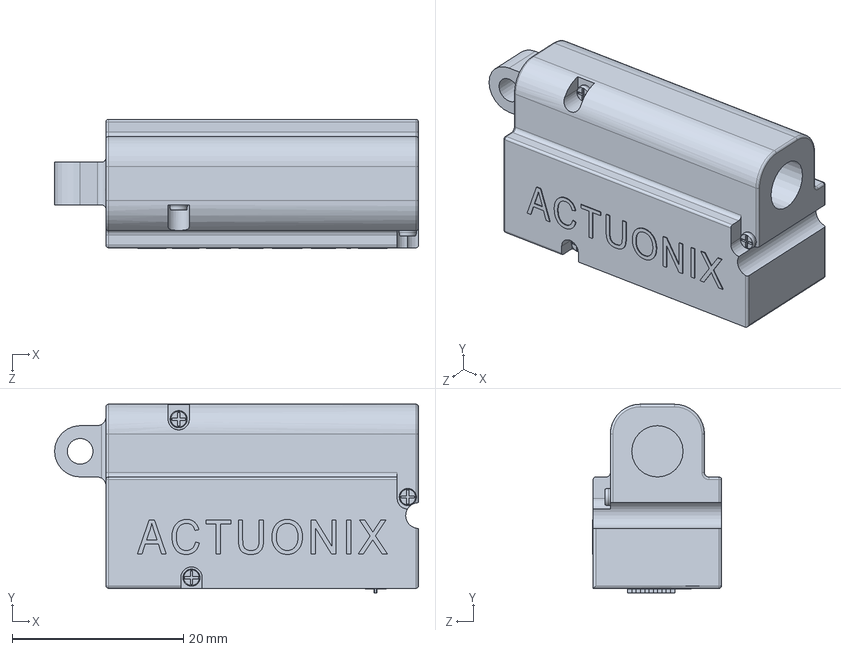
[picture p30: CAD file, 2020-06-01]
Hardware/SOLIDWORKS FILES/Actuonix PQ12-100-12-P-Housing.SLDPRT
42.5 x 22.0 x 15.1 mm

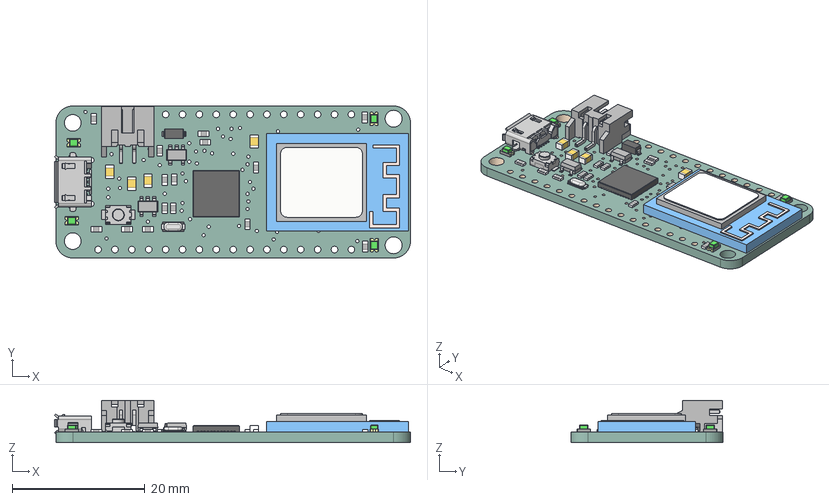
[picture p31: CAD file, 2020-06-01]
Hardware/SOLIDWORKS FILES/3010 Adafruit Feather M0 WiFi.step
53.5 x 22.9 x 6.37 mm
Board
10uF x 4
1k x 15
GREEN x 4
SPST_TACT-KMR2
microUSB
MCP73831T-2ACI/OT x 2
MBR120
1X16_ROUND
JSTPH
ATSAMD21G18_QFN
ATWINC1500_MR210PA
FEATHERLOGO

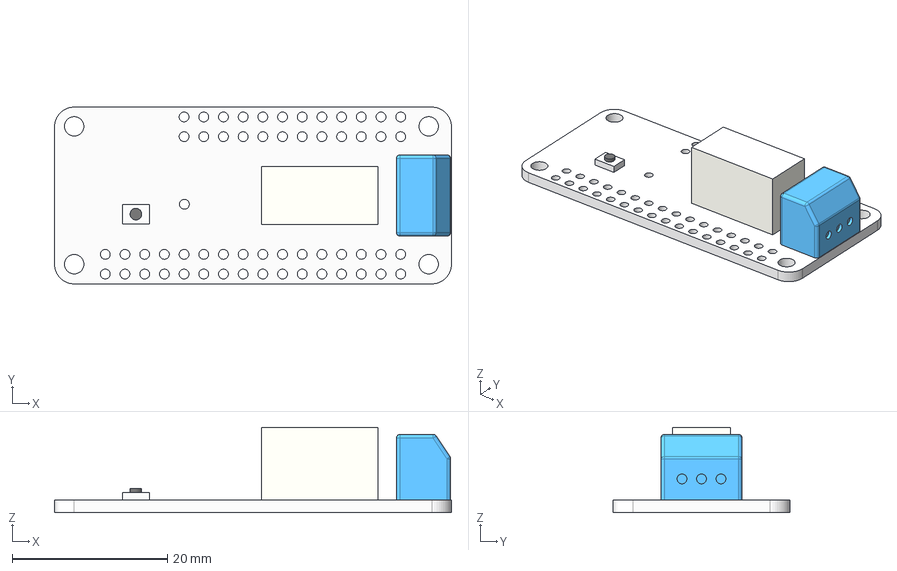
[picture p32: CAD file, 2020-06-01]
Hardware/SOLIDWORKS FILES/2895 Relay Feather Wing (1).step
51.2 x 22.8 x 11.0 mm

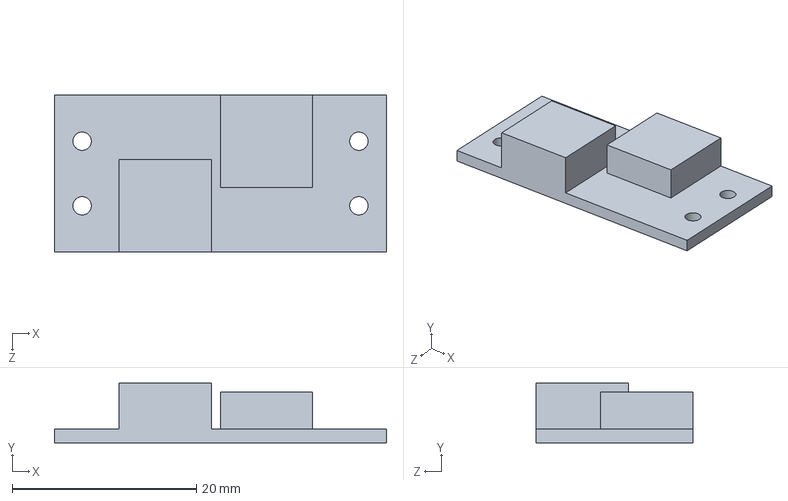
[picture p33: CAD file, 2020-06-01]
Hardware/SOLIDWORKS FILES/DCDC Boost.SLDPRT
36.0 x 6.50 x 17.0 mm

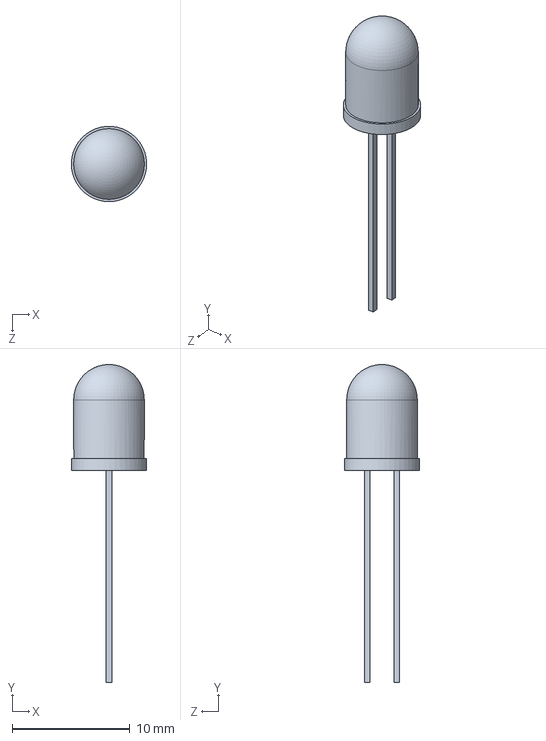
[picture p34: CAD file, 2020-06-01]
Hardware/SOLIDWORKS FILES/LED v1.SLDPRT
6.40 x 27.0 x 6.40 mm

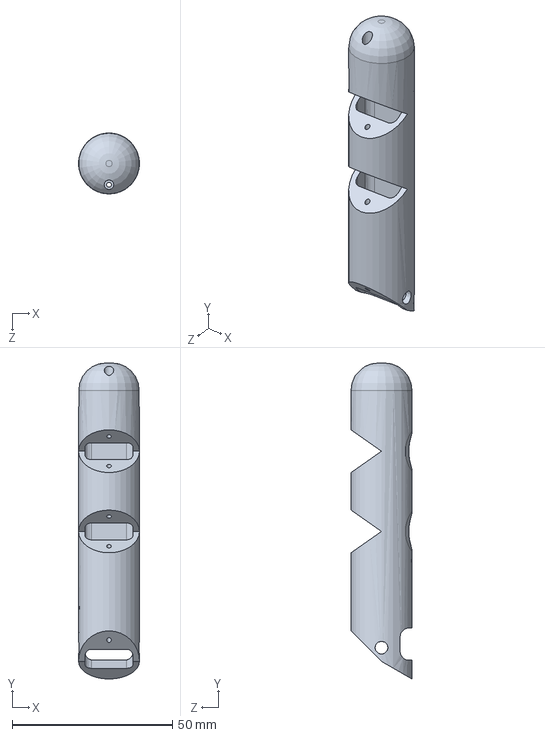
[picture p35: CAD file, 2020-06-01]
Hardware/SOLIDWORKS FILES/FLEXIFINGER v4.SLDPRT
19.0 x 98.5 x 19.0 mm

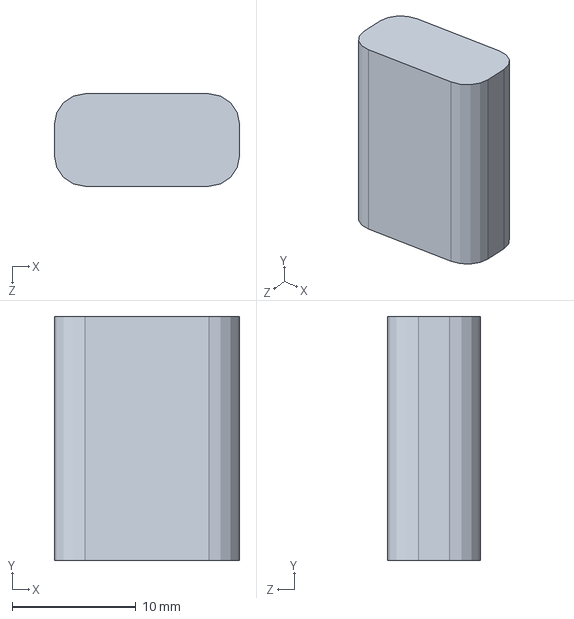
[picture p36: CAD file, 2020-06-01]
Hardware/SOLIDWORKS FILES/PHALANGE 2 v4.SLDPRT
15.0 x 19.8 x 7.50 mm

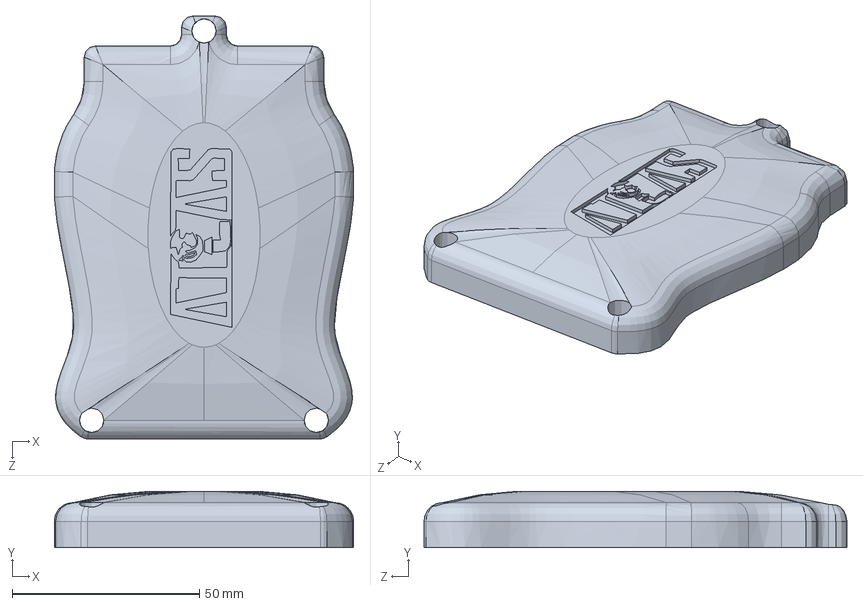
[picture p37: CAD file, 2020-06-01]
Hardware/SOLIDWORKS FILES/COVER v5.SLDPRT
80.0 x 15.0 x 113.0 mm

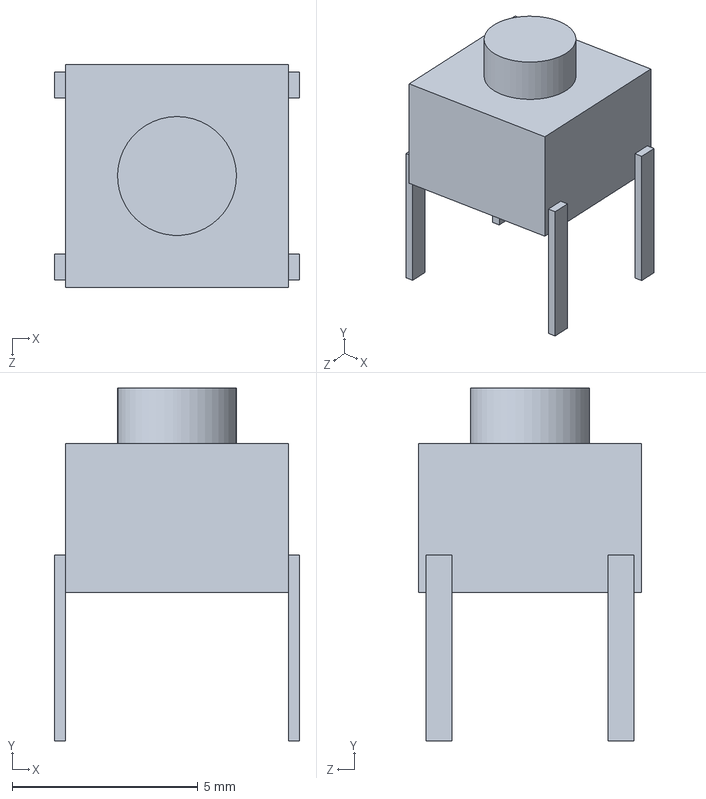
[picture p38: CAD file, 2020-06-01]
Hardware/SOLIDWORKS FILES/Switch v1.SLDPRT
6.60 x 9.50 x 6.00 mm

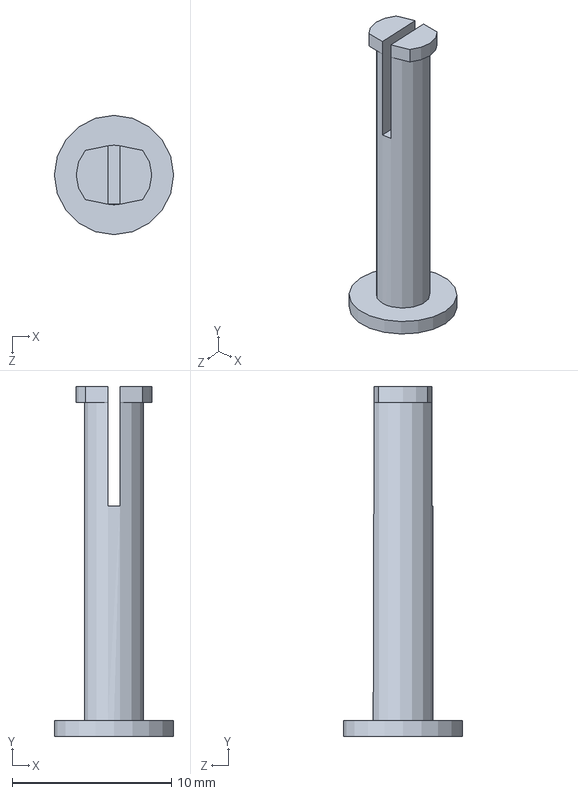
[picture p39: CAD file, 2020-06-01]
Hardware/SOLIDWORKS FILES/pin knuckle.SLDPRT
7.50 x 22.0 x 7.50 mm

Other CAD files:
Hardware/SOLIDWORKS FILES/Adafruit Relay.SLDPRT
Hardware/SOLIDWORKS FILES/Actuonix PQ12-100-12-P-Shaft.SLDPRT
Hardware/SOLIDWORKS FILES/Mid Plate.SLDPRT
Hardware/SOLIDWORKS FILES/Battery v1.SLDPRT
Hardware/SOLIDWORKS FILES/PHALANGE 1 v4.SLDPRT
Hardware/SOLIDWORKS FILES/PHALANGE 3 v4.SLDPRT

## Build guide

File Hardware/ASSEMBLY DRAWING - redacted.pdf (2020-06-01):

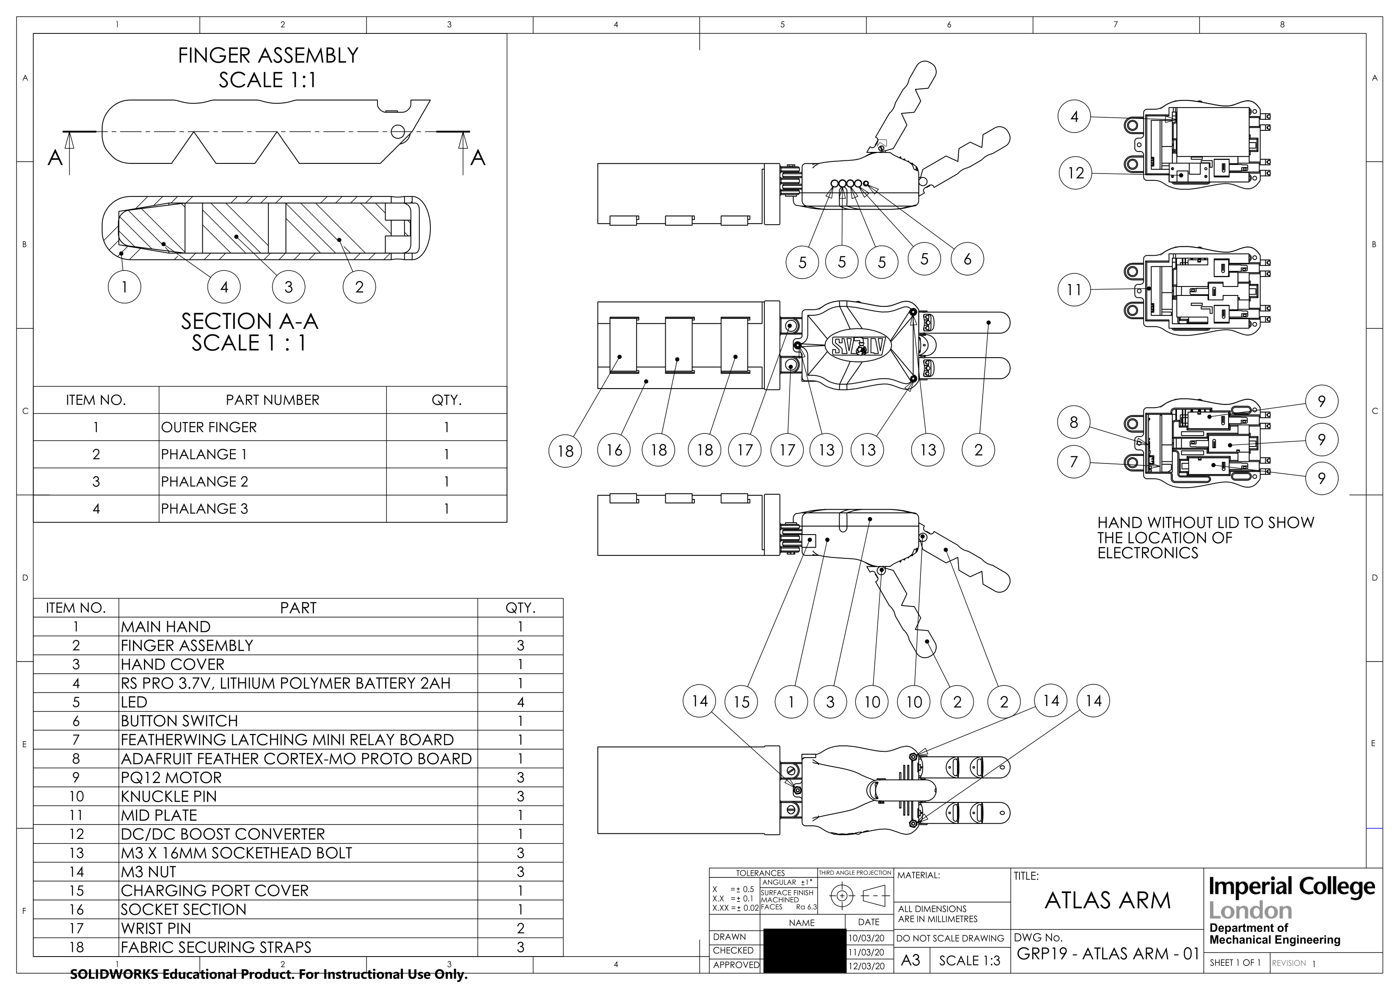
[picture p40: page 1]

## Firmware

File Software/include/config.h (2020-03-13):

/*
This file allocates meaningful names to the pins on the board.
All functions in this project use these names, so, if we want to wire the 
board differently, we only need to change this file
*/

#ifdef __cplusplus
extern "C" {
#endif

#ifndef config_H
#define config_H

// Power button pin
#define powerButton 5

// Battery voltage pin
#define VBATPIN A7

// Sensors are connected to analogue inputs 0 and 1
#define bicepSensor A0
#define tricepSensor A1
#define potentiometer A2

// motors for each finger connected to pins 10,11,12
#define thumb 10
#define index_finger 11
#define second_finger 12

// LED lights
#define LED1 1 // red LED for lowest battery level
#define LED2 0
#define LED3 22
#define LED4 23 // green LED for highest battery level

// Relay pins
#define relayhigh 21
#define relaylow 20

#ifdef __cplusplus
}
#endif

#endif

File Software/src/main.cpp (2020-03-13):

/*
Software for group 19 ME3 DMT project
This project is to develop a low-cost, 3D printable MMG prosthetic hand,
ATLAS

02.02.20
*/
/******************************************************************************/
//include statements and boilerplate code

#include <Arduino.h>
#include <ArduinoLowPower.h>
#include <filters.h>

#include "config.h"
#include "signal_classification.h"
#include "actuation.h"
#include "debugging.h"
#include "power_button.h"
/******************************************************************************/
// Define Global variables here

// This is the number of samples averaged over, tune this for performance
const int SAMPLES = 500;

// This is the current position we are at in the raw array
int position = 0;

// Here we store the current pose and state of each muscle
int bicepState = 0;
int tricepState = 0;
int pose = 0;

// here we store the sum of the squares for processing
long bicep_sum_squares = 0;
long tricep_sum_squares = 0;

// Here we declare the global arrays to store the raw signals
short bicepFiltered[SAMPLES];
short tricepFiltered[SAMPLES];

// Parameters for the filters
const float low_cutoff_freq = 100.0; //high cutoff frequency in Hz
const float high_cutoff_freq = 5;    // low cutoff frequency in Hz
const float sampling_time = 0.001;   //Sampling time in seconds.
IIR::ORDER order = IIR::ORDER::OD4;  // 4th order filter

// Filters for Bicep measurements
Filter bicepLowPass(low_cutoff_freq, sampling_time, order);
Filter bicepHighPass(high_cutoff_freq, sampling_time, order, IIR::TYPE::HIGHPASS);

// Filters for Tricep measurements
Filter tricepLowPass(low_cutoff_freq, sampling_time, order);
Filter tricepHighPass(high_cutoff_freq, sampling_time, order, IIR::TYPE::HIGHPASS);

/******************************************************************************/

/******************************************************************************/
// setup function, runs once when device is booted
void setup()
{
  init_motor();
  init_debug();
  init_UI();

  // When the button is pressed the device wakes up and performs the routine
  LowPower.attachInterruptWakeup(powerButton, wakeUpRoutine, FALLING);
}

/******************************************************************************/
// main loop of the program
void loop()
{

  buttonHandler();
  int THRESHOLD = analogRead(potentiometer) / 10;

  //unsigned long starttime = micros();

  // collect and filter the raw bicep data
  float bicepLP = bicepLowPass.filterIn(analogRead(bicepSensor));
  int newBicepFiltered = bicepHighPass.filterIn(bicepLP);

  // store old data temporarily and replace it with new data
  short oldBicepFiltered = bicepFiltered[position % SAMPLES];
  bicepFiltered[position % SAMPLES] = newBicepFiltered;

  // find the RMS of the filtered data
  bicep_sum_squares -= oldBicepFiltered * oldBicepFiltered;
  bicep_sum_squares += newBicepFiltered * newBicepFiltered;
  int bicepRMS = sqrt(bicep_sum_squares / SAMPLES);

  // determine the state of the muscle and store the old one
  int oldBicepState = bicepState;
  bicepState = muscleStatus(bicepRMS, oldBicepState, THRESHOLD);

  // collect and filter the raw tricep data
  float tricepLP = tricepLowPass.filterIn(analogRead(tricepSensor));
  int newTricepFiltered = tricepHighPass.filterIn(tricepLP);

  // store old data temporarily and replace it with new data
  short oldTricepFiltered = tricepFiltered[position % SAMPLES];
  tricepFiltered[position % SAMPLES] = newTricepFiltered;

  // find the RMS of the filtered data
  tricep_sum_squares -= oldTricepFiltered * oldTricepFiltered;
  tricep_sum_squares += newTricepFiltered * newTricepFiltered;
  int tricepRMS = sqrt(tricep_sum_squares / SAMPLES);

  // determine the state of the muscle and store the old one
  int oldTricepState = tricepState;
  tricepState = muscleStatus(tricepRMS, oldTricepState, THRESHOLD);

  // increment our position in the raw array
  position++;

  // check if there has been any change in muscle state
  if ((bicepState != oldBicepState) | (tricepState != oldTricepState))
  {
    // calculate new pose and actuate
    pose = classifySignal(pose, bicepState, tricepState);
    select_pose(pose);
  }

  print_to_plotter(bicepRMS, tricepRMS, THRESHOLD);
  //print_to_plotter(bicepRaw[position % SAMPLES]);
  //unsigned long finishtime = micros();
  /*if ((finishtime - starttime) < 1000)
    {
      digitalWrite(19, HIGH);
    }
    */
}

/******************************************************************************/

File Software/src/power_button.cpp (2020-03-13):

/*
This file contains all the functions necessary for the device's button

Upon a single click, the button will show the battery level and upon a 
long click it will put the device into sleep mode

18.02.20
 */
#include <Arduino.h>
#include <ArduinoLowPower.h>
#include "power_button.h"
#include "config.h"

// variable to decide whether the device is asleep or awake, 0 is on ,1 is sleep
int device_state = 0;

// function to poll the button to determine if it's been pressed and what type
// of press, then to call the necessary functions
// (horribly long and should be refactored in future)
void buttonHandler(void)
{
    // stores button state: 0 is up, 1 is down
    static int button_state;
    // stores whether battery level is being displayed (0 or 1)
    static int display_state;
    // stores time when button was first pressed down
    static unsigned long pressed_time;
    // stores time when battery level was first displayed
    static unsigned long display_time;

    // first check if we are currently showing the battery level
    if (display_state == 1)
    {
        // if battery level has been shown for more than 1 second
        if (millis() - display_time >= 1000)
        {
            // Turn off lights
            turnOffLED();
            // Set display state back to zero
            display_state = 0;
        }
    }
    else
    {
        // if button not previously pressed down
        if (button_state == 0)
        {
            // check if button has been pressed
            if (digitalRead(powerButton) == HIGH)
            {
                // set time for when button was pressed and set state to 1
                pressed_time = millis();
                button_state = 1;
            }
        }
        // if button has been previously pressed
        if (button_state == 1)
        {
            // check if button has been released yet
            if (digitalRead(powerButton) == LOW)
            {
                // if long press of button (over 1s)
                if (millis() - pressed_time >= 1000)
                {
                    // set state back to zero and put to sleep
                    button_state = 0;
                    device_state = 1;
                    putToSleep();
                }
                // if short press of button (< 1s)
                else
                {
                    // set state back to zero and display battery level
                    button_state = 0;
                    display_state = 1;
                    display_time = millis();

                    float measuredvbat = analogRead(VBATPIN);
                    measuredvbat *= 2;
                    measuredvbat *= 3.3;  // Multiply by 3.3V, reference voltage
                    measuredvbat /= 1024; // convert to voltage
                    // Battery has max voltage 4.2, nominal 3.7 and cut off 2.75
                    //  display level on 4 LEDS
                    displayBatteryLevel();
                }
            }
        }
    }
}

// Routine for when turned on from sleep mode
void wakeUpRoutine(void)
{
    if (device_state == 1)
    {
        // Blink LEDs three times
        for (int i = 0; i < 10; i++)
        {
            digitalWrite(LED1, HIGH);
            digitalWrite(LED2, HIGH);
            digitalWrite(LED3, HIGH);
            digitalWrite(LED4, HIGH);
            delay(50);
            digitalWrite(LED1, LOW);
            digitalWrite(LED2, LOW);
            digitalWrite(LED3, LOW);
            digitalWrite(LED4, LOW);
            delay(50);
        }

        //now, use relay
        for (int i = 0; i < 1; i++)
        {
            digitalWrite(relayhigh, HIGH);
            delay(500);
            digitalWrite(relayhigh, LOW);
            delay(500);
        }
        device_state = 0; // reset device state variable
    }
}

// Function to turn off relay and put the device into sleep mode
void putToSleep(void)
{
    openRelay();

    // Blink LEDs three times
    for (int i = 0; i < 3; i++)
    {
        digitalWrite(LED1, HIGH);
        digitalWrite(LED2, HIGH);
        digitalWrite(LED3, HIGH);
        digitalWrite(LED4, HIGH);
        delay(50);
        digitalWrite(LED1, LOW);
        digitalWrite(LED2, LOW);
        digitalWrite(LED3, LOW);
        digitalWrite(LED4, LOW);
        delay(50);
    }
    // now sleep
    LowPower.sleep();
}

void turnOffLED(void)
{
    digitalWrite(LED1, LOW);
    digitalWrite(LED2, LOW);
    digitalWrite(LED3, LOW);
    digitalWrite(LED4, LOW);
}

void init_UI(void)
{
    pinMode(LED1, OUTPUT);
    pinMode(LED2, OUTPUT);
    pinMode(LED3, OUTPUT);
    pinMode(LED4, OUTPUT);
    pinMode(powerButton, INPUT);

    pinMode(relayhigh, OUTPUT);
    pinMode(relaylow, OUTPUT);

    closeRelay();
}

void displayBatteryLevel(void)
{
    float measuredvbat = analogRead(VBATPIN);
    measuredvbat *= 2;
    measuredvbat *= 3.3;  // Multiply by 3.3V, reference voltage
    measuredvbat /= 1024; // convert to voltage
    // Battery has max voltage 4.2, nominal 3.7 and cut off 2.75
    //  display level on 4 LEDS
    if (measuredvbat > 2.75)
    {
        digitalWrite(LED1, HIGH);
    }
    if (measuredvbat > 3.1)
    {
        digitalWrite(LED2, HIGH);
    }
    if (measuredvbat > 3.5)
    {
        digitalWrite(LED3, HIGH);
    }
    if (measuredvbat > 3.8)
    {
        digitalWrite(LED4, HIGH);
    }
}

void openRelay(void)
{
    // put relay code here
    for (int i = 0; i < 1; i++)
    {
        digitalWrite(relaylow, HIGH);
        delay(500);
        digitalWrite(relaylow, LOW);
        delay(500);
    }
}

void closeRelay(void)
{
}

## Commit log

2020-02-11 filter not working
2020-02-18 moved filter and included lowpower lib
2020-03-02 power button funcs continued
2020-06-01 added solidworks files
    [2895 Relay Feather Wing (1).step, 3010 Adafruit Feather M0 WiFi.step, Actuonix PQ12-100-12-P-Housing.SLDPRT, Actuonix PQ12-100-12-P-Shaft.SLDPRT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]
